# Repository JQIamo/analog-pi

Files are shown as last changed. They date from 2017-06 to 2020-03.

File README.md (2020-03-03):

# analog-pi
Analog PI controller with > 10MHz bandwidth. Design by Joe Tiamsuphat.

For full documentation of the circuit, see the [manual](https://github.com/JQIamo/analog-pi/blob/master/pi/Documents/PI_Manual.pdf).
Please read the manual very carefully, especially the section "Initial Calibration" at page 14. A wrong calibration could result in damaging the circuit's output stages.

**NOTE:** The PI controller [manual](https://github.com/JQIamo/analog-pi/blob/master/pi/Documents/PI_Manual.pdf) is out of date. It should still be used as a reference, but it does not document several new features. Please look at issues [#2](https://github.com/JQIamo/analog-pi/issues/2) and [#3](https://github.com/JQIamo/analog-pi/issues/3) for more information. 

## File description

* `/fab/*`: Ready-made files for immediate fabrication. There is the main PI board (`pi_v2.5.3`), and three "shield" boards which make assembly into the box (located in `/fab/EnclosureDesign_v2.5.3_CAD`) easier. See below for description.
* `/pi/*`: Design files for the main PI board, including documentation, schematics, simulations, etc. The schematic/board layout are done in NI Multisim + Ultiboard.
* `/pi-frontpanel/*`: Eagle board files for a frontpanel "shield" board
* `/pi-pots/*`: Eagle board files for potentiometers which set the gains, output offset, sweep amplitude.
* `/pi-shield/*`: Eagle board file for adapter shield between PI board and the POTs/Frontpanel breakout boards.

Total cost is in the neighborhood of $1k per completed box (includes professionally populated PCBs, enclosure, power supply, etc.), although that number would depend on quantity ordered, whether you populate the boards yourself, etc.

## Enclosure

There is a Protocase Designer file (in `/fab/EnclosureDesign_v2.5.3_CAD`

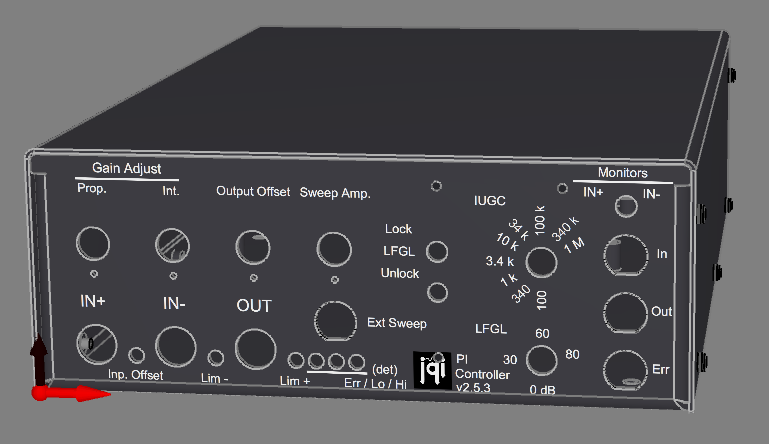
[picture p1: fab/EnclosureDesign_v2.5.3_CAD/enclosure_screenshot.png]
enclosure


Other auxiliary parts:

| Name | Part number | supplier |
|-------|------------|-------|
| FuseDrawer | 486-1342-ND | Digikey|
|Fuse	|F2393-ND|	Digikey|
|PwrEntry	|486-1302-ND	|Digikey
HexStandoff	|36-4802-ND|	Digikey
KnurledKnob	|226-3084-ND	|Digikey
POT Dial|	987-1002-ND	|Digikey
Isolated BNC	|ARFX1905-ND	|Digikey
PowerSupply	|179-2302-ND|	Digikey

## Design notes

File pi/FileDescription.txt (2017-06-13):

\Design\
   EnclosureDesign\			       -Enclosure design for version 2.4.1, 2.5.1, .2.5.2
      PanelCutout\                 -Sketchup: Enclosure cut-out designs
	  PI_EnclosureParts.xlsx       -Excel: Bill of Material for enclosure
   Gerber\                         -Gerber RS-274X, NC drill, Part-centroid export from PI.ewprj
   PartsDatabase\                  -MultiSim: Database containing parts schematics, footprints,
                                    and simulation models
   PartsMap\                       -Layout location map of resistors, capacitors, and IC.
   PI.ewnet                        -Ultiboard: netlist from Multisim to Ultiboard
   PI.ewprj                        -Ultiboard: Layout file
   PI.ms12                         -MultiSim: Schematic file
   PI_BOM_1MRInputImpedance.xlsx   -MS Excel: Bill of Material for PCB (1MOhm input impedance)
   PI_BOM_50RInputImpedance.xlsx   -MS Excel: Bill of Material for PCB (50Ohm input impedance)
   PI_Layout.pdf                   -PDF: Printout PCB layout images
   PI_Schematic.pdf                -PDF: Printout schematic design
\Document\
   PartsManual\                    -PDF: Data sheets of parts used in the project.
   TestResults2.5.1Mod\            -Test results of Modified2.5.1 (similar to 2.5.2)
   TestResults2.5Mod\              -Test results of Modified2.5 (similar to 2.5.1)
   PI_BodePlot.pxt                 -IGOR Pro: Interactive Bode plot of
                                    PI controller output response at different settings
   PI_Manual.docx                  -MS Word: Manual
   PI_Manual.pdf                   -PDF: Printout Manual
\Simulation\                       -MultiSim: Test simulations for models and designs
\FileDescription.txt               -Text: file description in the project
\VersionLog.txt                    -Text: Current version and change log

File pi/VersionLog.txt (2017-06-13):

Version 2.5.3

+ Add J9 low profile jumper to disable input offset.
+ Change part number for input offset POT (POT11) to one with low thermal coefficient. Adds ~$15 to BOM cost.

Version 2.5.2

+ Change IUGC capacitance. Remove 15uF and 4.7uF, add 470pF and 150pF
+ Add relay to turn off I_VGA when unlock.
+ Adjust Integral Limiter: change feedback capacitance from 510pF to 1500pF,
  and remove output capacitors
+ Change output impedance of monitor ports (IN_MON, ERR_MON, OUT_MON) from 1kOhm to 20 Ohms
  With 1 kOhm output impedance, monitor signals bandwidth are slower than the actual signal.
  To avoid confusion, using 20 Ohms output impedance makes the monitor ports show actual signals.
  However, output resistors can be damaged if monitor port is shorted-circuit. 

Version 2.5.1

+ Install 2 parallel 100 Ohms at OUT to make 50 Ohms output impedance,
  mitigating impedance mismatch and signal reflections.
+ Change input resistors to 2 parallel 100 Ohms to make it possible to modify input impedance.
  User can choose to install +/-10V 1 MOhm input impedance or +/-10V 50 Ohms input impedance.
+ Change maximum P_GAIN from 3 to 10

Fix issues in version 2.5

+ Correct wiring at regulators L7912 and L7905
+ I_VGA and P_VGA trims cannot zero the output offset.
  Change resistance around trim pot from 10kOhms to 3kOhms.
+ Unable to turn off P_GAIN and I_GAIN completely.
  Control voltage need to be at least -1.0V to turn off.
  Change resistance around external pot from 20kOhms to 10kOhms
  Increase control range to +/-1.7V to make sure that VGA can be completely turned off
+ High frequency signal ~10MHz pass through the integrator and destructive interfere
  with proportional signal
  Change input resistance to Integrator from 1kOhm to 10kOhms to reduce direct transfer signal.
+ Switch MON_IN1 causes oscillation in ERR_MON
  Long trace ERR_MON to LockDector makes LM7171 unstable.
  Install 1kOhm resistor to isolate output from long trace.
+ POT4 Buffer Bandwidth control is too close to output BNC and does not provide gain
  bandwidth limit as expected.  When use in low bandwidth mode, phase margin becomes worse.
  Use high bandwidth mode and install a 3MHz low-pass filter before buffer U18
+ LM7171 in OUTPUT stage has resonant response at 25MHz.
  Long trace PI to LockDector and IntLimiter makes LM7171 unstable
  Install 1kOhm resistor to isolate output from long trace.
+ Switch bouncing (IUGC, LFGL, UNLOCK/LFGL/LOCK).
  Install low-pass filter to mitigate switch bouncing.  Install MOSFETs for driving relays.
+ IN_MON, ERR_MON, OUT_MON overshoot at high frequency when connect 1m cable to oscilloscope.
  Install 1kOhm isolation resistors at output.  Expect monitor ports to drive high impedance load.

Version 2.5
   A prototype that aim to fix low-gain DC-offset issue in version 2.4.1.
The design implements separation between Proportional and Integral signals.
The separation between proportional and integral gives advantages over combined implementation:
+ Proportional signal can be faster and less noisy with less op-amp stages (10MHz->25MHz).
+ Integral signal can have higher open loop gain (80dB->120dB), minimizing DC offset
  from reference signal even with low proportional gain setting.
+ Allowing more flexible setting for slow(integral) and fast(proportional) signals.

This version also implements experimental design for feedback integral limiter, and output limiter.

Fine input offset is removed to use potentiometer knob for integral gain.

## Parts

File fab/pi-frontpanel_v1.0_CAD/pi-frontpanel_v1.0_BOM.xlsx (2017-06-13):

Line | Qty | Value | Part Num | Source | Package | Parts | Notes
1 | 1 |  | 450-1536-ND | Digikey | SP3T_LUG | S8_LOCK_UNLOCK
2 | 1 |  | A1921-ND | Digikey | 1X02 | JP2
3 | 1 |  | MMBT2222A-FDICT-ND | Digikey | SOT23-BEC | T1
4 | 1 |  | S7086-ND | Digikey | 2X18 | JP1
5 | 2 | 4.99k | P4.99KFCT-ND | Digikey | R_1206 | R2, R3
6 | 1 | 14k | P14.0KFCT-ND | Digikey | R_1206 | R1
7 | 4 | BNC-V | A32262-ND | Digikey | BNC-V | ERR_MON, IN_MON, OUT_MON, SWEEP_IN
8 | 2 | MRA112 | 360-2368-ND | Digikey | MRA112 | IUGC, LFGL
9 | 1 | SPDT | 450-1523-ND | Digikey | SPDT_LUG | S7_MON_IN_SEL
10 | 1 | SSL-LX5093IGW | 67-2207-ND | Digikey | LED-TH | LED | This part needs to be soldered such that the bottom of the LED is 0.6" (1.5cm) above the PCB surface.

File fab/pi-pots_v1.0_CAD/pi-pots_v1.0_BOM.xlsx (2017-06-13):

Line | Qty | Value | Part Num | Source | Package | Parts | Notes
1 | 4 | BOURNS-3590P | 3590P-1-103L-ND | Digikey | SP3T_LUG | I_GAIN, OUTPUT_OFFSET, P_GAIN, SWEEP_AMP
2 | 2 | PINHD-3X4 | 952-2121-ND | Digikey | 3x02 | J1 | This is a subassembly. Two 3x2 male headers are placed on bottom as marked on PCB.

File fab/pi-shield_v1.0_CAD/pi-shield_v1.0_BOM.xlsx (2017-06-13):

Line | Qty | Value | Part Num | Source | Package | Parts | Notes
1 | 1 |  | S2111EC-18-ND | Digikey | 2X18/90 | JP1
2 | 5 |  | S7000-ND | Digikey | 1X02 | J1_SWP_EXT, J4_IN_MON, J5_ERR_MON, J6_OUT_MON, LED1
3 | 2 |  | S7008-ND | Digikey | 1X10 | S5_IUGC, S6_LFGL
4 | 7 |  | S7036-ND | Digikey | 1X03 | J8_POW, POT7_SWP_AMP, POT8_OUT_OFFSET, POT9_IGAIN, POT10_PGAIN, S7_INPUT_MON_SW, S8_LOCK_UNLOCK
5 | 1 |  | A19470-ND | Digikey | 1X03 | J8_POW1
6 | 2 |  | S7071-ND | Digikey | 3X04 | J1 | This is a subassembly. Two 3x2 female headers are placed as marked on PCB.

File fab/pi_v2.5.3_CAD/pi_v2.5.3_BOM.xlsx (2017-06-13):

Quantity | Description | RefDes | Manufacturer | Manufacturer Part No. | Vendor | Vendor Part No. | Package | Type | Price | Total Price
3 | BNC | J2, J3, J7 | TE Connectivity | 1-1337543-0 | Digikey | A97553-ND | Ultiboard\1-1337543-0 | TH | 2.03000 | 6.09000
2 | HDR, HDR1X10 | S5, S6 | TE Connectivity | 1-640454-0 | Digikey | A19437-ND | Ultiboard\HDR_1-640454-0 | TH | 0.50000 | 1.00000
5 | HDR, HDR1X2 | J1, J4, J5, J6, LED1 | TE Connectivity | 640454-2 | Digikey | A19423-ND | Ultiboard\HDR_640454-2 | TH | 0.13000 | 0.65000
7 | HDR, HDR1X3 | J8, POT7, POT8, POT9, POT10, S7, S8 | TE Connectivity | 640454-3 | Digikey | A19430-ND | Ultiboard\HDR_640454-3 | TH | 0.17000 | 1.19000
1 | HDR, HDR1x3, 2mm low profile | J9 | Sullins Connector Solutions | NRPN031PAEN-RC | Digikey | S5800-03-ND | Ultiboard\HDR_2mm_3 | TH | 0.35000 | 0.35000
1 | POTENTIOMETER, ACCUTRIM 1280 | POT11 | Vishay Foil Resistors | Y005610K0000K0L | Digikey | 804-1021-ND | Ultiboard\3006P | TH | 17.84000 | 17.84000
5 | POTENTIOMETER, 3006P | POT4, POT5, POT6, POT12, POT13 | Bourns Inc. | 3006P-1-103LF | Digikey | 3006P-103LF-ND | Ultiboard\3006P | TH | 2.08000 | 10.40000
3 | POTENTIOMETER, 3296W | POT1, POT2, POT3 | Bourns Inc. | 3296W-1-102LF | Digikey | 3296W-102LF-ND | Ultiboard\3296W | TH | 2.41000 | 7.23000
4 | SWITCH, G5V-1-DC12 | S1, S2, S3, S4 | Omron Electronics Inc-EMC Div | G5V-1-DC12 | Digikey | Z774-ND | Ultiboard\G5V-1Relay | TH | 2.05000 | 8.20000
19 | CAPACITOR, 0.015uF | C35, C36, C37, C38, C39, C40, C41, C42, C43, C44, C45, C46, C47, C48, C49, C50, C51, C52, C115 | Murata Electronics North America | GRM155R71E153KA61D | Digikey | 490-3251-1-ND | Ultiboard\0402 | SMD | 0.03200 | 0.60800
1 | CAPACITOR, 0.047uF | C114 | Taiyo Yuden | TMK105B7473KV-F | Digikey | 587-2240-1-ND | Ultiboard\0402 | SMD | 0.01900 | 0.01900
92 | CAPACITOR, 0.15uF | C1, C2, C3, C4, C5, C6, C7, C11, C12, C13, C14, C15, C16, C17, C18, C19, C20, C23, C24, C25, C26, C31, C32, C33, C34, C53, C54, C55, C56, C57, C58, C59, C60, C61, C62, C63, C64, C65, C66, C67, C68, C69, C70, C71, C72, C73, C74, C75, C76, C77, C78, C79, C80, C81, C82, C83, C84, C85, C86, C87, C88, C89, C90, C91, C92, C93, C94, C95, C96, C97, C98, C109, C110, C113, C120, C121, C122, C123, C124, C125, C126, C127, C128, C129, C130, C131, C132, C133, C134, C135, C136, C137 | Samsung Electro-Mechanics America, Inc | CL10B154KA8SFNC | Digikey | 1276-1970-1-ND | Ultiboard\0603 | SMD | 0.01200 | 1.10400
1 | CAPACITOR, 0.47uF | C112 | Taiyo Yuden | TMK107B7474KA-TR | Digikey | 587-2670-1-ND | Ultiboard\0603 | SMD | 0.07200 | 0.07200
1 | CAPACITOR, 1.5uF | C111 | TDK Corporation | C1608X5R1E155K080AB | Digikey | 445-5962-1-ND | Ultiboard\0603 | SMD | 0.24000 | 0.24000
4 | CAPACITOR, 1500pF | C8, C9, C10, C117 | Murata Electronics North America | GRM155R71H152KA01J | Digikey | 490-6354-1-ND | Ultiboard\0402 | SMD | 0.02300 | 0.09200
9 | CAPACITOR, 150pF | C101, C102, C103, C104, C105, C106, C107, C108, C119 | Murata Electronics North America | GRM1555C1H151JA01D | Digikey | 490-3229-1-ND | Ultiboard\0403 | SMD | 0.03000 | 0.27000
8 | CAPACITOR, 15uF | C21, C22, C27, C28, C29, C30, C99, C100 | TDK Corporation | C2012X5R1V156M125AC | Digikey | 445-14423-1-ND | Ultiboard\0805 | SMD | 0.68900 | 5.51200
1 | CAPACITOR, 4700pF | C116 | Murata Electronics North America | GRM155R71E472KA01D | Digikey | 490-1309-1-ND | Ultiboard\0402 | SMD | 0.02100 | 0.02100
1 | CAPACITOR, 470pF | C118 | Murata Electronics North America | GRM1555C1H471JA01D | Digikey | 490-1297-1-ND | Ultiboard\0402 | SMD | 0.10000 | 0.10000
3 | MOSFET, 2N7002E | T1, T2, T3 | ON Semiconductor | 2N7002ET1G | Digikey | 2N7002ET1GOSCT-ND | Ultiboard\SOT-23-3 | SMD | 0.14000 | 0.42000
1 | OPAMP, BUF634 | U18 | Texas Instruments | BUF634U/2K5 | Digikey | 296-24142-1-ND | Ultiboard\SOIC8 | SMD | 8.13000 | 8.13000
1 | OPAMP, LM239 | U20 | Texas Instruments | LM239DR | Digikey | 296-14590-1-ND | Ultiboard\SOIC14 | SMD | 0.43000 | 0.43000
9 | OPAMP, LM7171 | U2, U5, U7, U10, U13, U16, U17, U28, U29 | Texas Instruments | LM7171AIMX/NOPB | Digikey | 296-35428-1-ND | Ultiboard\SOIC8 | SMD | 3.11100 | 27.99900
14 | OPAMP, OPA172 | U8, U12, U14, U15, U19, U21, U22, U23, U24, U25, U26, U27, U31, U32 | Texas Instruments | OPA172IDR | Digikey | 296-37237-1-ND | Ultiboard\SOIC8 | SMD | 1.68500 | 23.59000
4 | OPAMP, THS4631 | U1, U3, U4, U6 | Texas Instruments | THS4631D | Digikey | 296-17626-5-ND | Ultiboard\SOIC8 | SMD | 10.55000 | 42.20000
2 | OPAMP, VCA824 | U9, U11 | Texas Instruments | VCA824ID | Digikey | 296-22898-5-ND | Ultiboard\SOIC14 | SMD | 9.45000 | 18.90000
35 | RESISTOR, 100kΩ | R51, R52, R70, R71, R73, R74, R77, R78, R85, R86, R87, R88, R89, R90, R92, R93, R96, R97, R98, R99, R100, R101, R102, R103, R104, R109, R114, R115, R116, R117, R118, R119, R120, R121, R122 | Rohm Semiconductor | MCR03ERTF1003 | Digikey | RHM100KCFCT-ND | Ultiboard\0603 | SMD | 0.00840 | 0.29400
3 | RESISTOR, 100Ω | R64, R65, R66 | Vishay Thin Film | PHP01206E1000BST5 | Digikey | PHP100ACT-ND | Ultiboard\VTFR1206 | SMD | 3.53000 | 10.59000
13 | RESISTOR, 10kΩ | R25, R36, R42, R53, R54, R55, R56, R81, R82, R83, R84, R91, R107 | Rohm Semiconductor | MCR03ERTF1002 | Digikey | RHM10.0KCFCT-ND | Ultiboard\0603 | SMD | 0.01100 | 0.14300
1 | RESISTOR, 10MΩ | R113 | Rohm Semiconductor | MCR03ERTJ106 | Digikey | RHM10MCGCT-ND | Ultiboard\0603 | SMD | 0.01000 | 0.01000
22 | RESISTOR, 1kΩ | R15, R16, R17, R18, R26, R29, R40, R45, R46, R48, R49, R50, R57, R58, R59, R60, R69, R75, R76, R79, R80, R105 | Vishay Beyschlag | MCT06030C1001FP500 | Digikey | MCT0603-1.00K-CFCT-ND | Ultiboard\0603 | SMD | 0.06900 | 1.51800
3 | RESISTOR, 1MΩ | R3, R10, R111 | Samsung Electro-Mechanics America, Inc | RC1608F105CS | Digikey | 1276-3487-1-ND | Ultiboard\0603 | SMD | 0.01400 | 0.04200
10 | RESISTOR, 20Ω | R5, R12, R19, R24, R30, R35, R43, R44, R47, R61 | Rohm Semiconductor | MCR03ERTF20R0 | Digikey | RHM20CFCT-ND | Ultiboard\0603 | SMD | 0.01100 | 0.11000
1 | RESISTOR, 300kΩ | R110 | Rohm Semiconductor | MCR03ERTF3003 | Digikey | RHM300KCFCT-ND | Ultiboard\0603 | SMD | 0.01100 | 0.01100
2 | RESISTOR, 30kΩ | R72, R108 | Rohm Semiconductor | MCR03ERTF3002 | Digikey | RHM30KCFCT-ND | Ultiboard\0603 | SMD | 0.01100 | 0.02200
9 | RESISTOR, 3kΩ | R20, R21, R22, R23, R27, R33, R34, R37, R106 | Rohm Semiconductor | MCR03ERTF3001 | Digikey | RHM3.00KCFCT-ND | Ultiboard\0603 | SMD | 0.01100 | 0.09900
1 | RESISTOR, 3MΩ | R112 | Rohm Semiconductor | MCR03ERTJ305 | Digikey | RHM3MCGCT-ND | Ultiboard\0603 | SMD | 0.01000 | 0.01000
18 | RESISTOR, 402Ω | R1, R2, R6, R7, R8, R9, R13, R14, R31, R32, R38, R39, R62, R63, R67, R68, R94, R95 | Vishay Thin Film | PHP00603E4020BST1 | Digikey | 764-1092-1-ND | Ultiboard\VTFR0603 | SMD | 1.35440 | 24.37920
2 | RESISTOR, 604Ω | R28, R41 | Rohm Semiconductor | MCR03ERTF6040 | Digikey | RHM604CLCT-ND | Ultiboard\0603 | SMD | 0.01100 | 0.02200
5 | SWITCH, ADG1412 | S9, S10, S11, S12, S13 | Analog | ADG1412YRUZ | Digikey | ADG1412YRUZ-ND | Ultiboard\TSSOP16 | SMD | 7.17000 | 35.85000
13 | SWITCHING_DIODE, MMBD1203 | D1, D2, D3, D4, D5, D6, D7, D8, D9, D10, D11, D12, D13 | Fairchild Semiconductor | MMBD1203 | Digikey | MMBD1203CT-ND | Ultiboard\SOT-23-3 | SMD | 0.20500 | 2.66500
1 | VOLTAGE_REFERENCE, ADR445 | U30 | Analog Devices | ADR445ARZ | Digikey | ADR445ARZ-ND | Ultiboard\SOIC8 | SMD | 6.25000 | 6.25000
1 | VOLTAGE_REGULATOR, L7805 | U36 | STMicroelectronics | L7805ACD2T-TR | Digikey | 497-7253-1-ND | Ultiboard\D2PAK | SMD | 0.72000 | 0.72000
1 | VOLTAGE_REGULATOR, L7812 | U34 | STMicroelectronics | L7812ACD2T-TR | Digikey | 497-1177-1-ND | Ultiboard\D2PAK | SMD | 0.87000 | 0.87000
1 | VOLTAGE_REGULATOR, L7905 | U35 | STMicroelectronics | L7905CD2T-TR | Digikey | 497-1214-1-ND | Ultiboard\D2PAK | SMD | 0.87000 | 0.87000
1 | VOLTAGE_REGULATOR, L7912 | U33 | STMicroelectronics | L7912CD2T-TR | Digikey | 497-1215-1-ND | Ultiboard\D2PAK | SMD | 0.83000 | 0.83000
 |  |  |  |  |  |  |  |  |  | 267.96220
 | BOARD SUMMARY
 | Total number of unique parts | 45
 | SMD placements per board | 314
 | TH placements per board | 31

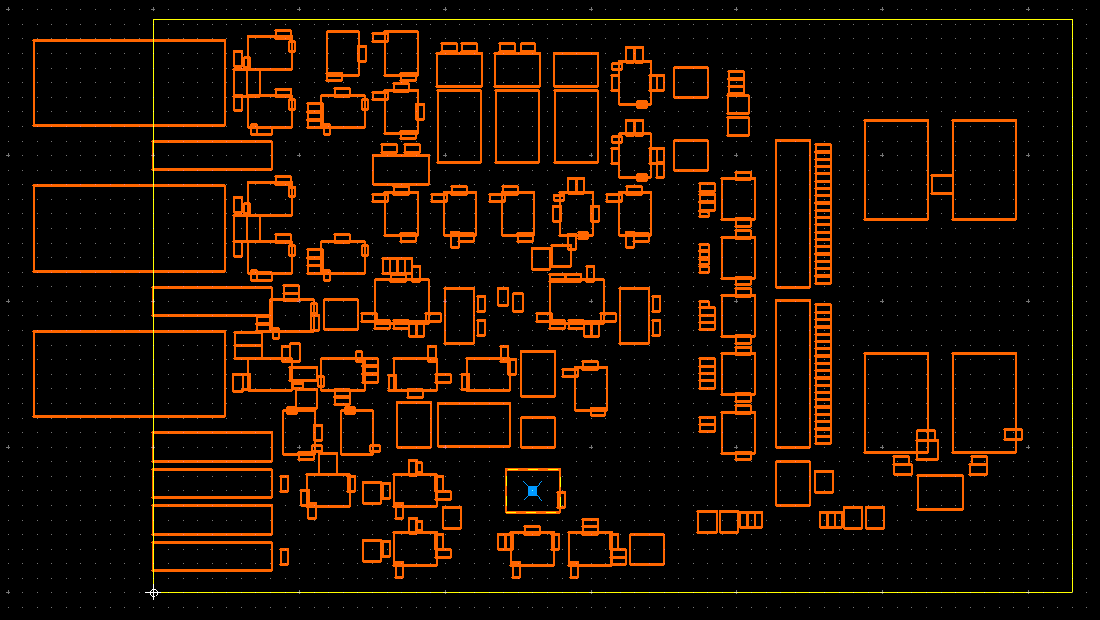
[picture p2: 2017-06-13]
pi/Design/PartsMap/ICMap/LM239.png

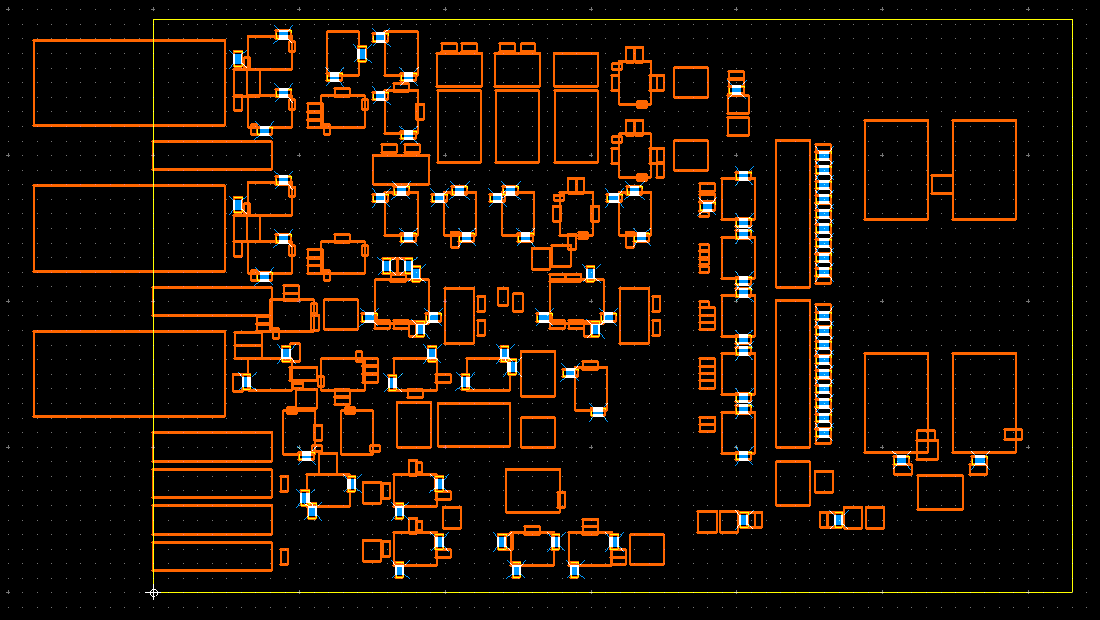
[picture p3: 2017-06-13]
pi/Design/PartsMap/CMap/0.15uF.png

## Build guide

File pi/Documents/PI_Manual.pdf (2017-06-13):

1

## PROPORTIONAL INTEGRAL CONTROLLER 2.5.2

## MANUAL

May 2016

Jiraphat Tiamsuphat
jt6ab@umd.edu

2

## Table of Contents

3

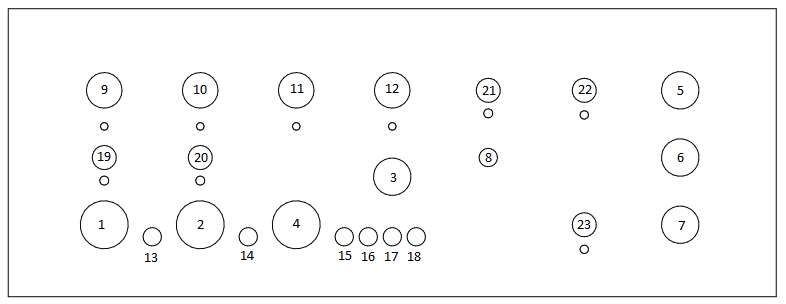
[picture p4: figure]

4

### Front Panel

Inputs

### 1. IN1 - Positive input (±10V, 1MΩ input impedance) 2. IN2 - Negative input (±10V, 1MΩ input impedance) 3. SWP_EXT - External sweep input (±10V, 10kΩ Input Impedance)

Outputs

### 4. OUT - PI filtered output signal (50Ω output impedance) 5. IN_MON - Monitor selected input voltage IN1/IN2 6. ERR_MON - Monitor error voltage 7. OUT_MON - Monitor output voltage

× ܯ_ =

Ω
Indicator

### 8. LED - lock indicator (Green/Red)

Controls
Potentiometer Knobs

### 9. I_GAIN - Integral gain control (Gain Range:0→10 with Dial: 20→80) 10. P_GAIN - Proportional gain control (Gain Range:0→10 with Dial: 20→80) 11. OUT_OFFSET - Output offset voltage control (±10.0V) 12. SWP_AMP - Sweep amplitude control

Front Panel Trimmer Potentiometers

### 13. IN_OFFSET - Input offset voltage control (±5.0V) 14. LO_LIMIT - Low limit of OUT (±10V) 15. HI_LIMIT - High limit of OUT (±10V) 16. ERR_DET - Absolute limit detection of error signal (Range: ±0→±1.5V) 17. LO_DET - Low limit detection of OUT 18. HI_DET - High limit detection of OUT

Switches

19. Unused switch (Fine input offset switch in version 2.4.1) 20. IN_MON_SEL (2 Positions) - Select to monitor IN1 (up) or IN2 (down) 21. LOCK/LFGL/UNLOCK (3 Positions) - Select filter mode 22. IUGC (9 Positions) - Select integral unity gain cutoff frequency 23. LFGL (9 Positions) - Select integral gain limit in LFGL mode

5

### Controls

Integral
I_GAIN
Continuous integral gain setting (I_GAIN: 0→10 with Dial: 20→80) In typical usage, I_GAIN should be set at 10 or as high as possible. IUGC (Integral Unity Gain Cutoff)
Select setting for integral unity gain cutoff
IUGC Unity Gain Cutoff frequency = (I_GAIN=3→10)
1* | 34 Hz → 100 Hz
2* | 100 Hz → 340 Hz
3* | 340 Hz → 1 kHz
4* | 1 kHz → 3.4 kHz
5 3.4 kHz → 10 kHz
6 10 kHz → 34 kHz
7 34 kHz → 100 kHz
8 100 kHz → 340 kHz
9† 340 kHz → 1 MHz
* Proportional gain must be turned off
† Proportional gain must be turned on
LFGL (Low Frequency Gain Limit)
Select setting for Low Frequency Gain Limit. Position LFGL = 20 Log(
| Ω ) (I_GAIN=3→10)
1 -10dB → 0dB
2 0dB → 10dB
3 10dB → 20dB
4 20dB → 30dB
5 30 dB → 40dB
6 40dB → 50dB
7 50 dB → 60dB
8 60 dB → 70dB
9 70 dB → 80dB

Determine Suitable Integral Settings
In negative feedback control scheme, high gain is required to make system signal close to equal the reference signal. Fast signal response is also desired to make system signal follow reference signal as fast as possible. However, if the gain of the feedback system is too high and too fast (gain higher than 0dB at 0 degree phase margin), the feedback system will become unstable and oscillate.

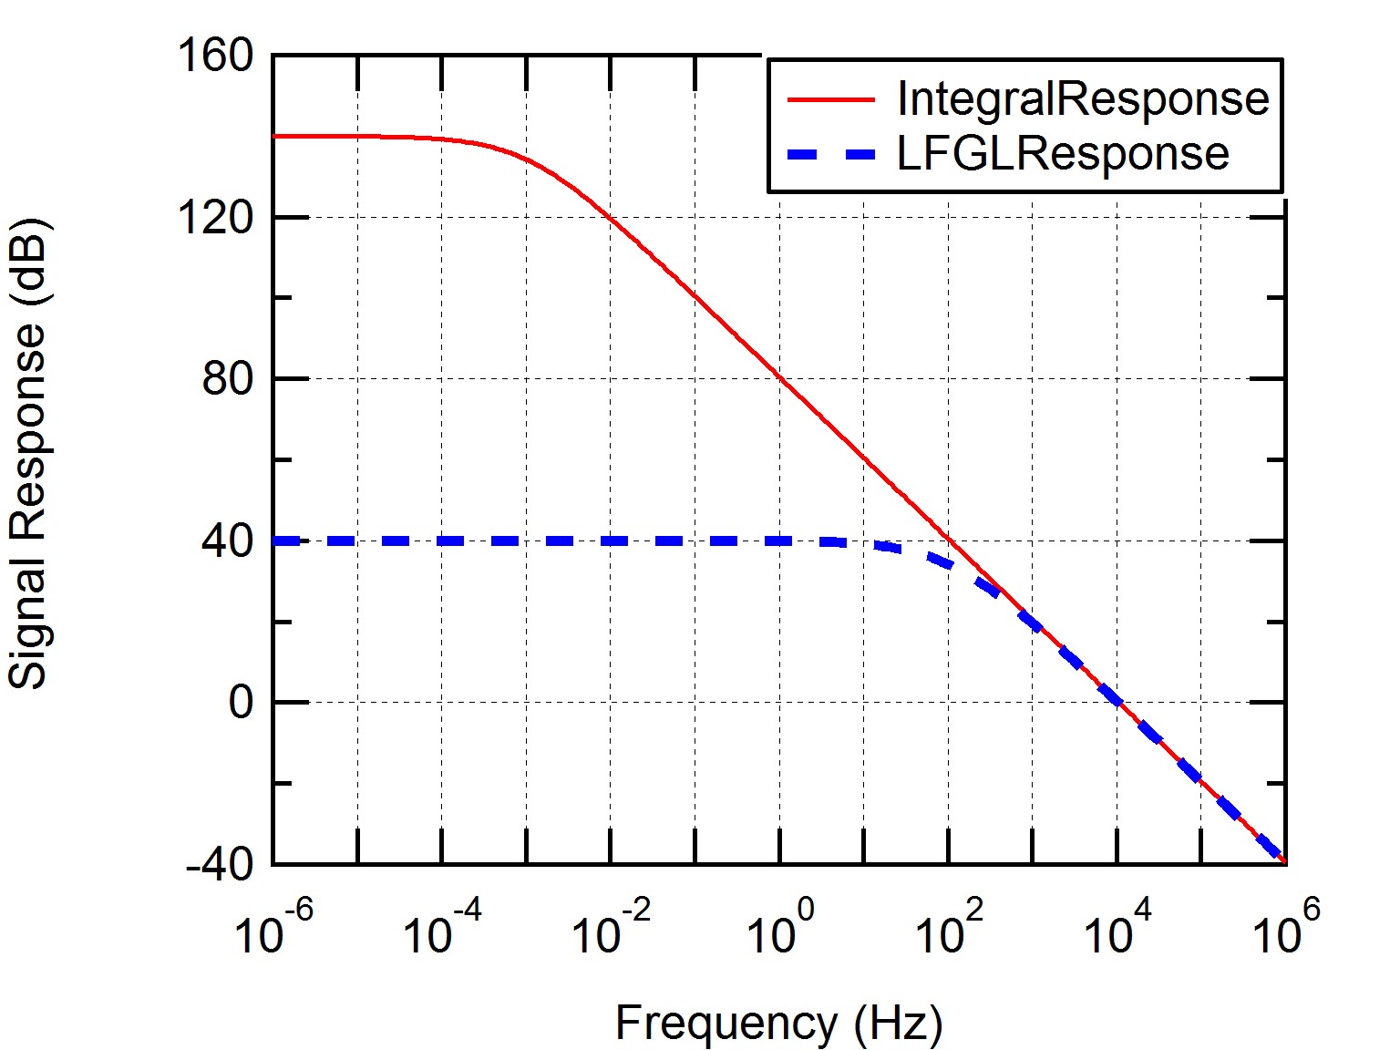
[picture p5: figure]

6

To find suitable Integral setting, first, try locking the system with the following setting I_GAIN=10, IUGC=8, LFGL=9, P_GAIN=0.
If the system oscillate with this setting, try the following
1. Set mode to LFGL and reduce LFGL setting.
2. Use lower IUGC setting and repeat 1.

### 3. Use lower I_GAIN setting (I_GAIN lower than 3 is not recommended)

If the system cannot be locked with the setting I_GAIN=1, IUGC=1, LFGL=1, P_GAIN=0, the system may be too slow to be locked with this controller.
Bode Plot of Integral Signal Response
The following are examples integral response at different settings. The interactive plotting code (Igor pro) can be found at \Documents\PI_BodePlot.pxt

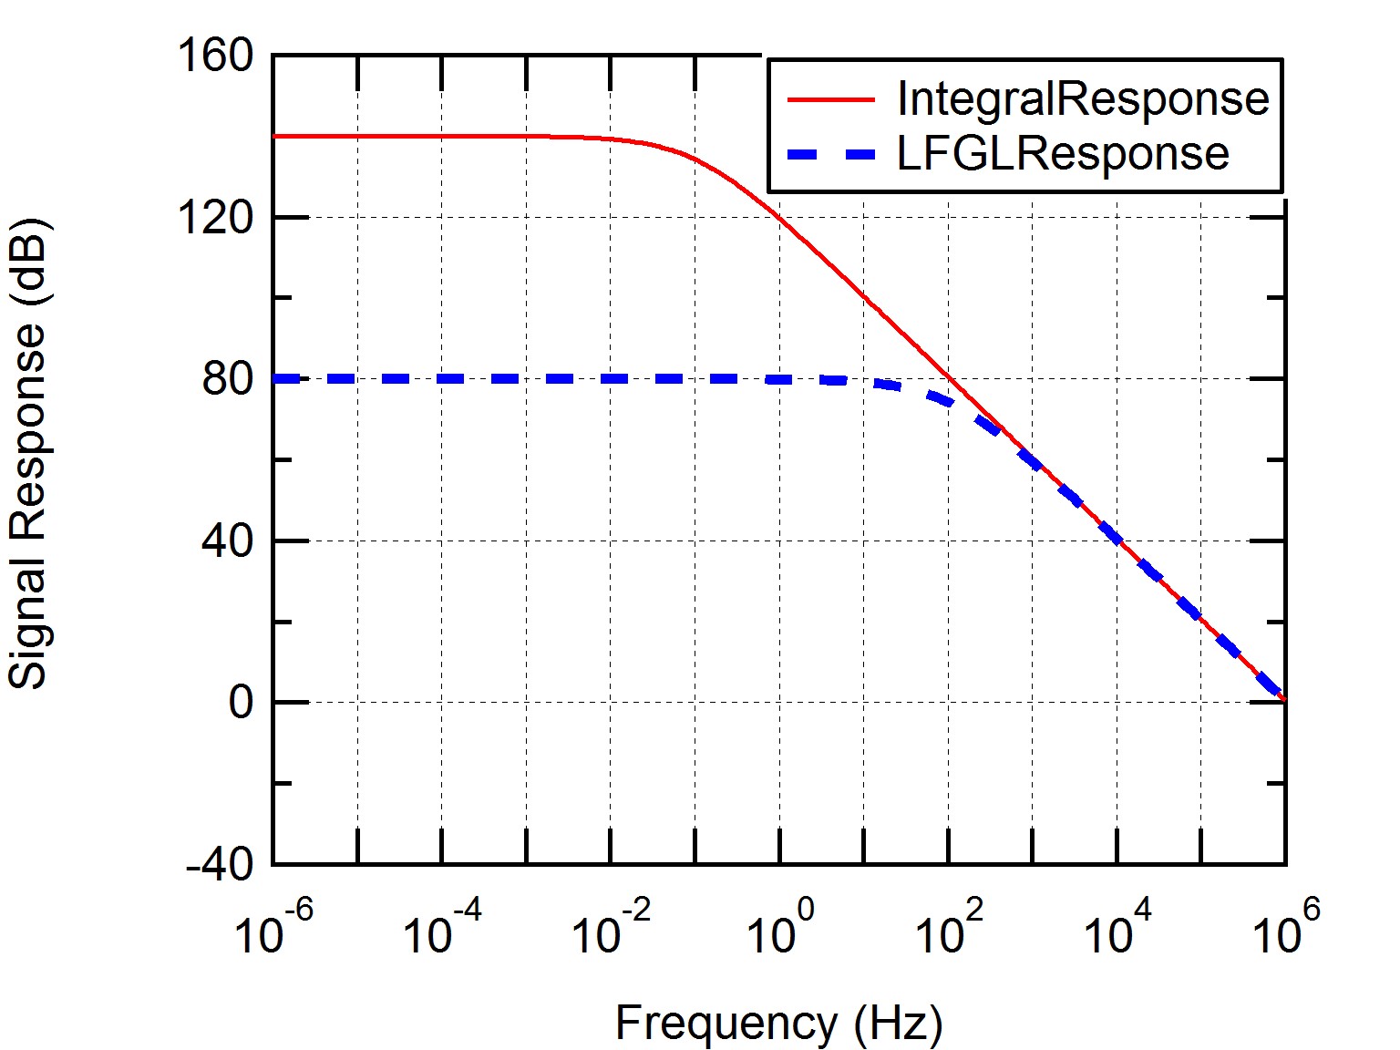
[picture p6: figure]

I_GAIN=10,
IUGC(9)=1MHz, LFGL(9)=80dB

I_GAIN=10,
IUGC(5)= 10kHz, LFGL(5)=40dB

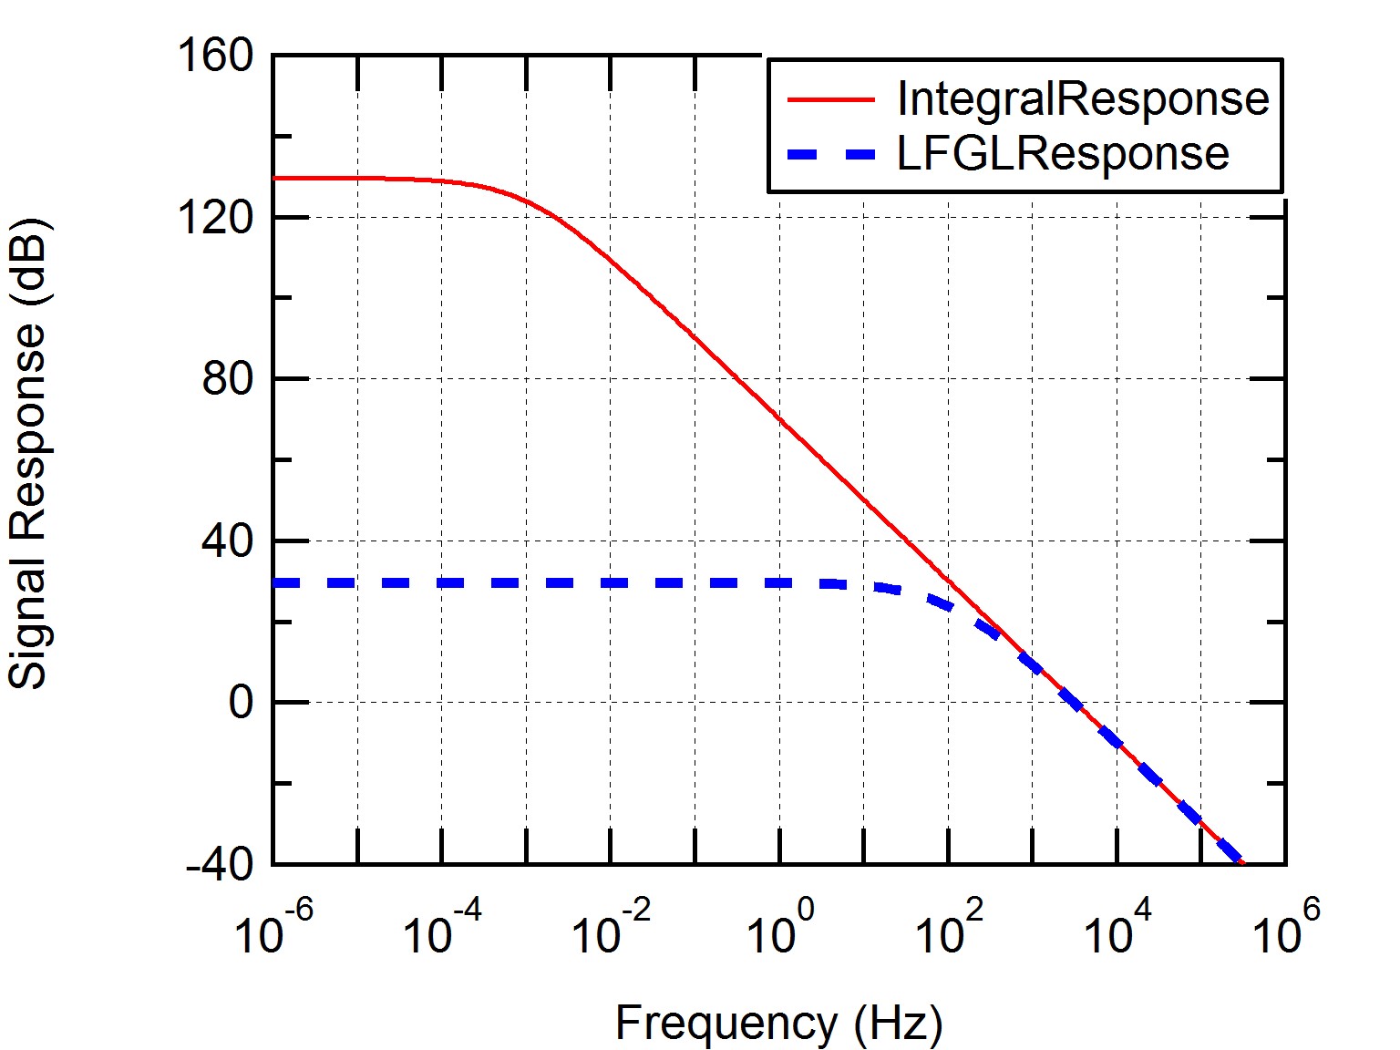
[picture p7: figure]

I_GAIN=3,
IUGC(5)= 3kHz, LFGL(5)=30dB

Proportional
P_GAIN
Continuous proportional gain setting (P_GAIN: 0→10 with Dial: 20→80)
While the integral signal has unity gain bandwidth up to 1 MHz, the proportional signal has unity gain bandwidth between 1 kHz to 10 MHz. Due to high speed nature of Proportional signal, if P_GAIN is too high (P_GAIN*SYSTEM_GAIN > 0dB), it may cause an oscillation on system that has response bandwidth less than 20MHz.
To find suitable P_GAIN setting, first, set P_GAIN=0 and lock the system using only the integral signal. Then, slowly increase P_GAIN until OUT start to oscillate. The suitable setting for P_GAIN is 90-95% of P_GAIN that makes OUT oscillate.

7

Operation Mode
UNLOCK: Switch Down
OUT is set by OUT_OFFSET, SWP_EXT, and SWP_AMP. Output scan is active
LFGL: Switch Middle
Output scan is active.
PI filter is active with limited low frequency gain
LOCK: Switch Up
Output scan is inactive.
PI filter is active with 120dB + I_GAIN[dB] low frequency gain. Operation Formula
ERR = IN1 − IN2 + IN_OFFSET
SWP = SWP_AMP × SWP_EXT
P = P_GAIN × (IN1 − IN2) | for signal frequency 100 Hz to 10MHz
UNLOCK: OUT = OUT_OFFSET + SWP
LFGL: | OUT = OUT_OFFSET + SWP + P + LFGL[I_GAIN × ERR]
LOCK: | OUT = OUT_OFFSET + P + INT[I_GAIN × ERR]
| LFGL is the integration with limited gain
| INT is the open-loop integration

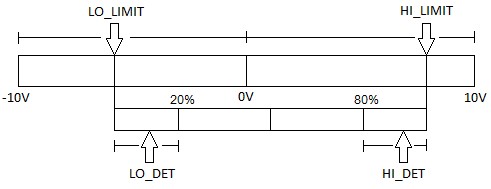
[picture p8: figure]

8

Miscellaneous Setting
LO_LIMIT/HI_LIMIT
The trim potentiometers set the low/high limit of OUT signal. To set the output range:

### 1. Disconnect IN1 and IN2, Monitor voltage value of OUT 2. Set filter mode to LOCK 3. Turn IN_OFFSET clockwise until OUT increases to high limit 4. Adjust HI_LIMIT to desire level 5. Turn IN_OFFSET counter-clockwise until OUT decreased to low limit 6. Adjust LO_LIMIT to desire level

ERR_DET
The LED indicator will become red if the value of ERR_MON is outside the range of ERR_DET (Variable Range: ±0→±4V).
LO_DET/HI_DET
The LED indicator will become red if the signal OUT is greater than HI_DET or lower than LO_DET. HI_DET can be set from 80% to 100% of output range. LO_DET can be set from 0% to 20% of output range.

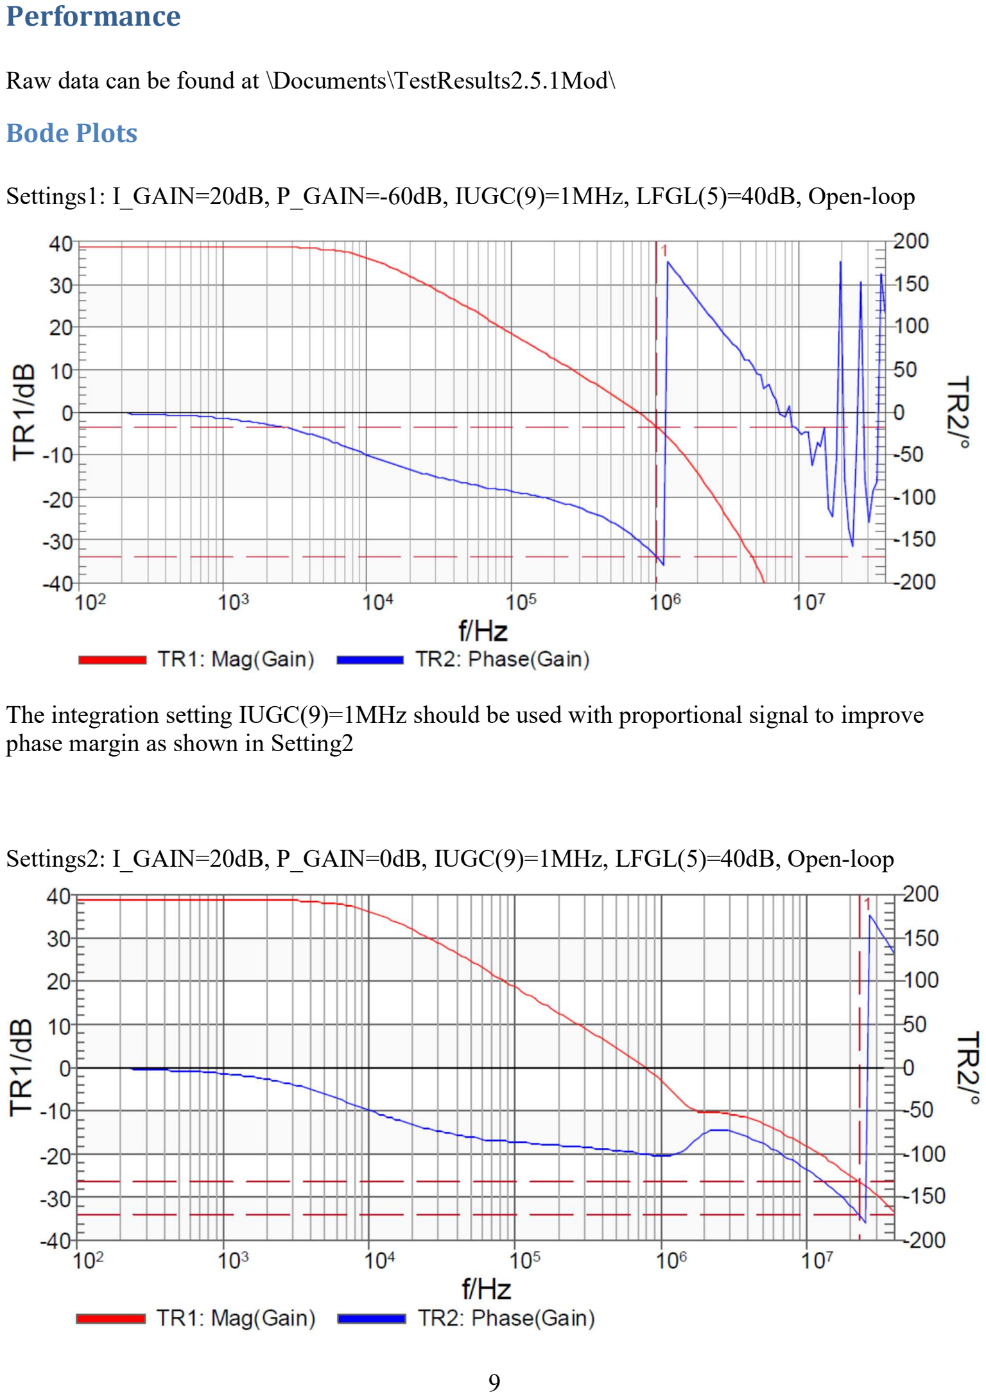
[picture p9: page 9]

9

### Performance

Raw data can be found at \Documents\TestResults2.5.1Mod\
Bode Plots
Settings1: I_GAIN=20dB, P_GAIN=-60dB, IUGC(9)=1MHz, LFGL(5)=40dB, Open-loop

The integration setting IUGC(9)=1MHz should be used with proportional signal to improve phase margin as shown in Setting2

Settings2: I_GAIN=20dB, P_GAIN=0dB, IUGC(9)=1MHz, LFGL(5)=40dB, Open-loop

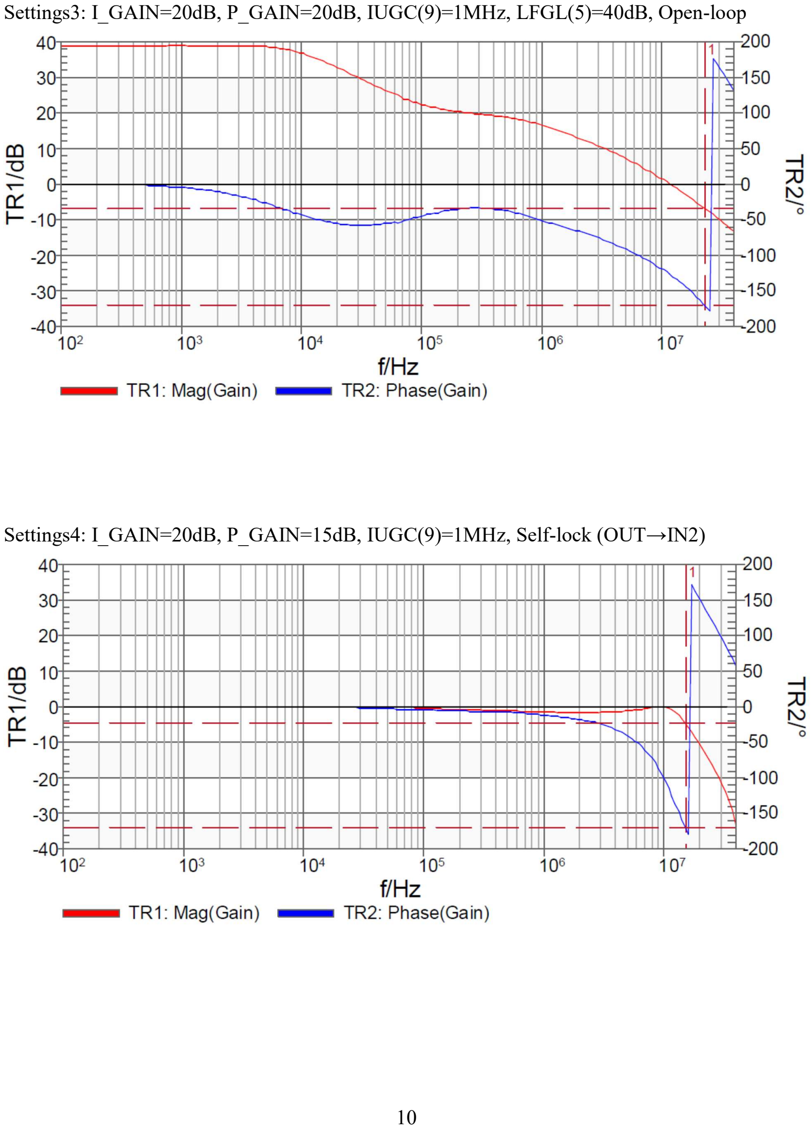
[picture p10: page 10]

10

Settings3: I_GAIN=20dB, P_GAIN=20dB, IUGC(9)=1MHz, LFGL(5)=40dB, Open-loop

Settings4: I_GAIN=20dB, P_GAIN=15dB, IUGC(9)=1MHz, Self-lock (OUT→IN2)

11

Self-Lock to Changing Reference
Use settings: I_GAIN=20dB, P_GAIN=10-20dB, IUGC(9)=1MHz, Self-lock (OUT→IN2) Blue: Reference signal (IN1)
Yellow: Reference Input monitor signal (IN1_MON)
Green: Output monitor signal (OUT_MON)

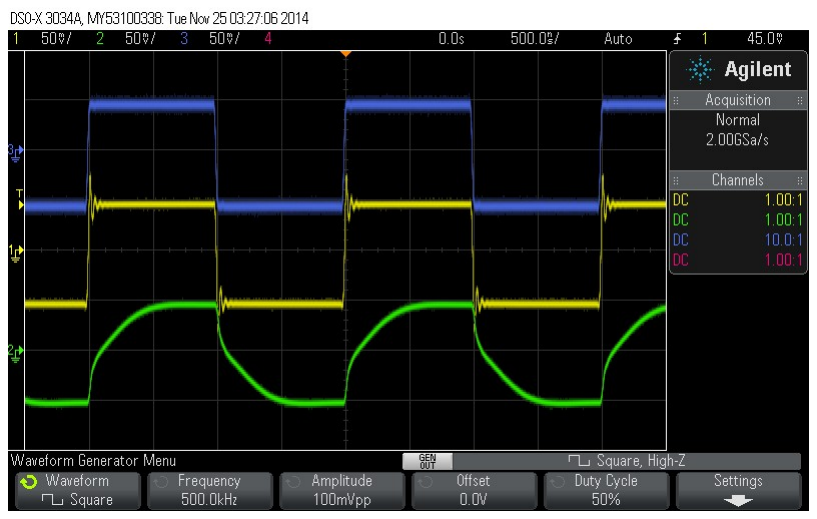
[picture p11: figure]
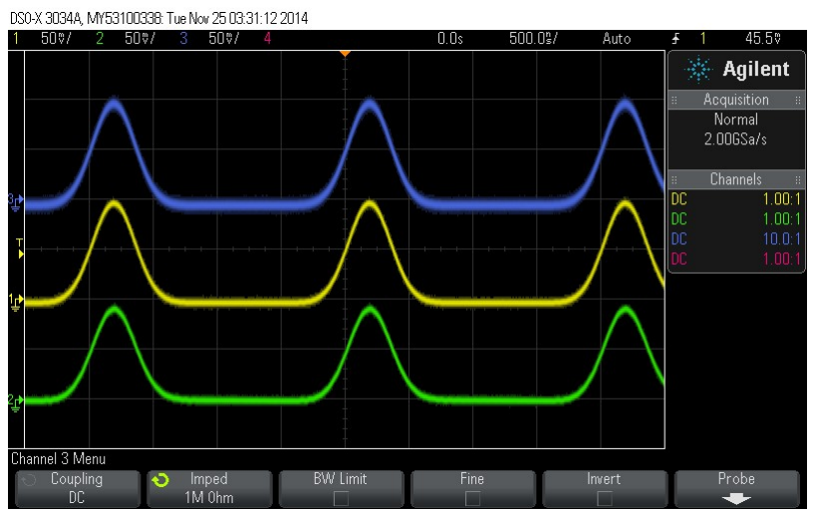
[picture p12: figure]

X-axis=500ns/div Y-axis=50mV/div | X-axis=500ns/div Y-axis=50mV/div

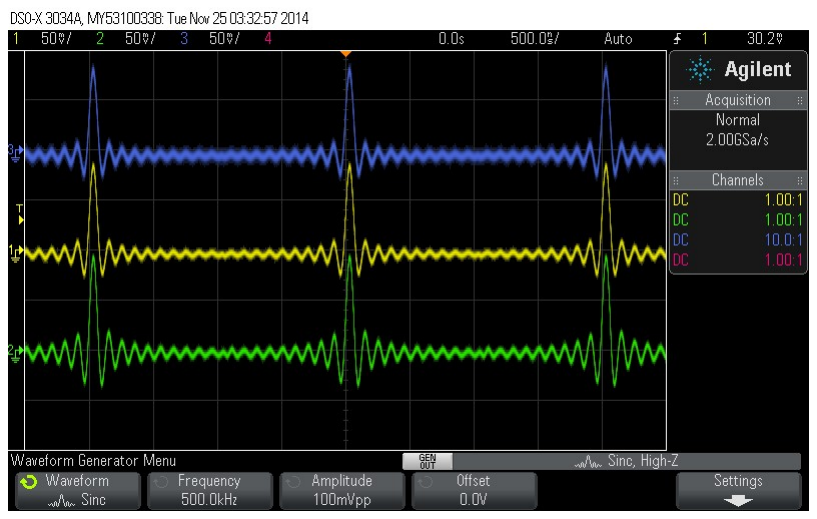
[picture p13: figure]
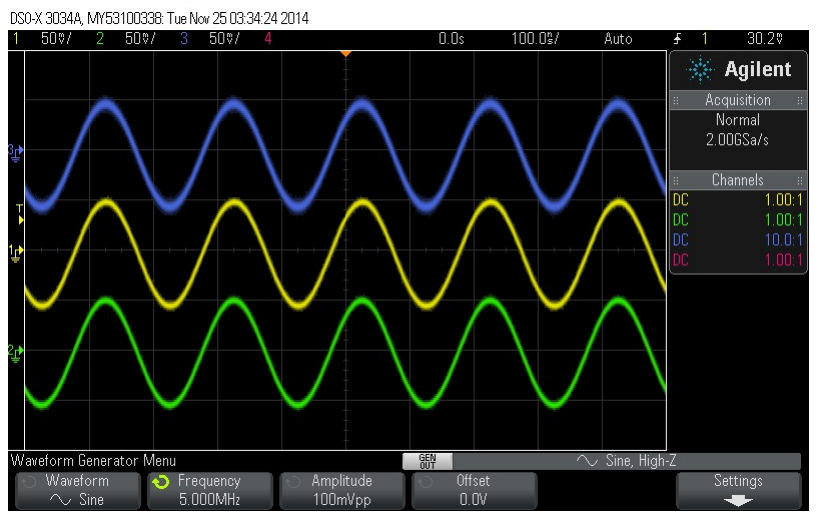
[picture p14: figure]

X-axis=500ns/div Y-axis: 50mV/div | X-axis=100ns/div Y-axis: 50mV/div
Test with large change in reference (±2.5V)
Yellow: Reference Input monitor signal (IN1_MON)
Green: Output monitor signal (OUT_MON)

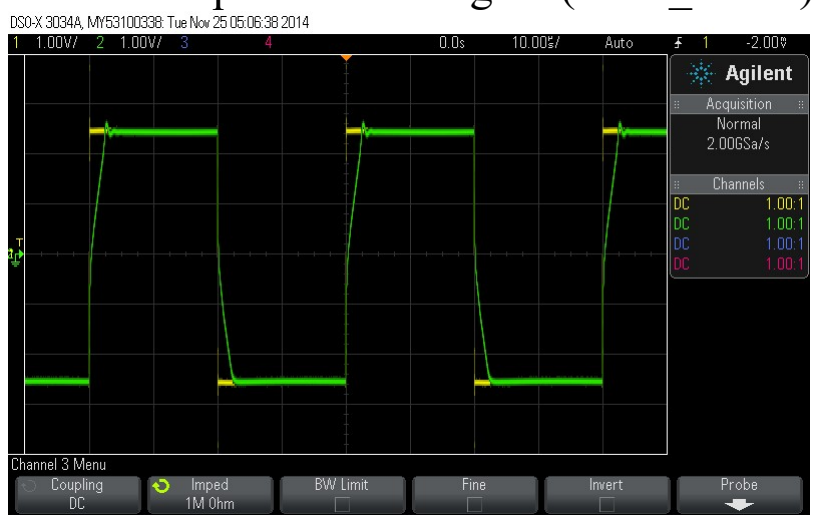
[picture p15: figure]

X-axis=10us/div Y-axis: 1V/div

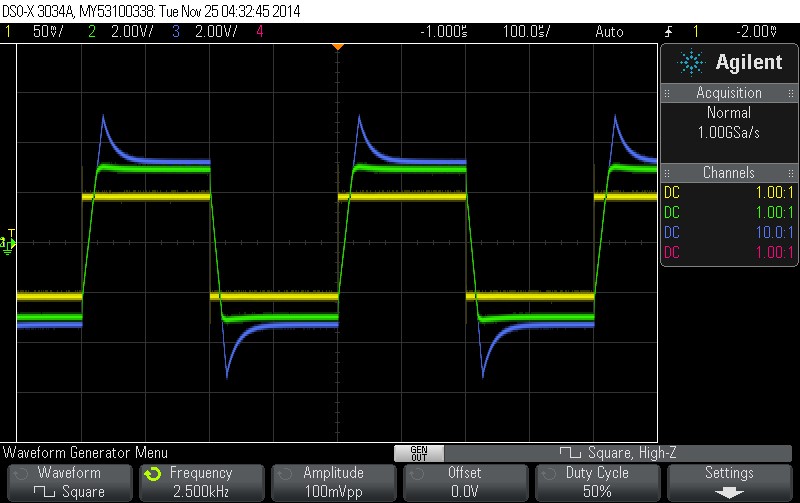
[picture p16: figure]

12

Integral Limiter and Output Limiter
Use settings: I_GAIN=20dB, P_GAIN=0dB, IUGC(9)=1MHz, LFGL(5)=40dB, Open-loop Set output high limit to +3V and output low limit to -3V
Yellow: Error monitor signal (ERR_MON)
Green: Output monitor signal (OUT_MON)
Blue: Output detection signal (OUT_DET)
OUT_DET is the output signal before output limiter; this signal is used for integral limiter.
When OUT_DET passes the output limits, it activates integral limiter that will stop the integrator from integrating signal further away from output limit. The output signal always stay inside the limit. However, OUT_DET may overshoot pass the output limit and recover back to stay slightly outside the output limit.

13

### Assembly

Front Panel Connection
RefDes | Front Panel Function
J1 | External Sweep
J4 | Input Monitor
J5 | Error Monitor
J6 | Output Monitor
LED1 | Red/Green LED
| 1 = GREEN P-doped (Anode)
| 2 = RED P-doped (Anode)
POT7 | Sweep Amplitude
POT8 | Output Offset
POT9 | Integral Gain
POT10 | Proportional Gain
S6 | Input Monitor Select
| 2→1 (D) = Monitor Input2
| 2→3 (U) = Monitor Input1
S4 | IUGC setting
| 1→2 = IUGC1
| 1→3 = IUGC2
| 1→4 = IUGC3
| 1→5 = IUGC4
| 1→6 = IUGC5
| 1→7 = IUGC6
| 1→8 = IUGC7
| 1→9 = IUGC8
| 1→10 = IUGC9
S5 | LFGL setting
| 1→2 = LFGL1
| 1→3 = LFGL2
| 1→4 = LFGL3
| 1→5 = LFGL4
| 1→6 = LFGL5
| 1→7 = LFGL6
| 1→8 = LFGL7
| 1→9 = LFGL8
| 1→10 = LFGL9
S7 | Unlock/LowFrequencyGainLimit/Lock
| SP3T Connections: Pin1→1, Pin2→2, Pin3→Pin5, Pin4→3
| 2→ (U) = Lock
| 2→3 (M) = LFGL
| 2→1 (D) = Unlock

14

Initial Calibrations and Tests
Power up:

### 1. Connect all front panel controls to the board 2. Connect OUT_MON to oscilloscope to monitor output voltage for initial testing 3. Turn on power supply to the board 4. The board should use around 300mA from +15V and 260mA from -15V. If you use test

power supply, set the current limit to 800mA to both +15V and -15V.
5. Change OUT_OFFSET to set OUT_MON to 0V.
Setup HI_LIMIT and LO_LIMIT:
6. Set mode to LOCK.
a. If OUT_MON decrease after set mode to LOCK, OUT_MON is at LO_LIMIT
b. If OUT_MON increase after set mode to LOCK, adjust IN_OFFSET CCW until OUT_MON decrease to LO_LIMIT

### 7. Change LO_LIMIT to set OUT_MON to -6V 8. Adjust IN_OFFSET CW until OUT_MON increase to HI_LIMIT 9. Change HI_LIMIT to set OUT_MON to +6V

Proportional VGA calibration: See picture next page

### 10. Set mode to UNLOCK 11. Use probe to measure the output pin (U9—Pin10) 12. Adjust the output of the VGA (U9—Pin10) to 0V with P_VGA_OUT_TRIM (POT2) 13. Set mode to LOCK, Set P_GAIN to maximum 14. Adjust the output of the VGA (U9—Pin10) to 0V with P_VGA_IN_TRIM (POT1)

Integral VGA calibration:

### 15. Measure OUT_MON voltage 16. Set mode to LFGL with this setting I_GAIN = 0, P_GAIN = 0, IUGC(7), LFGL(5) 17. Adjust OUT_MON to 0V with I_VGA_OUT_TRIM (POT3)

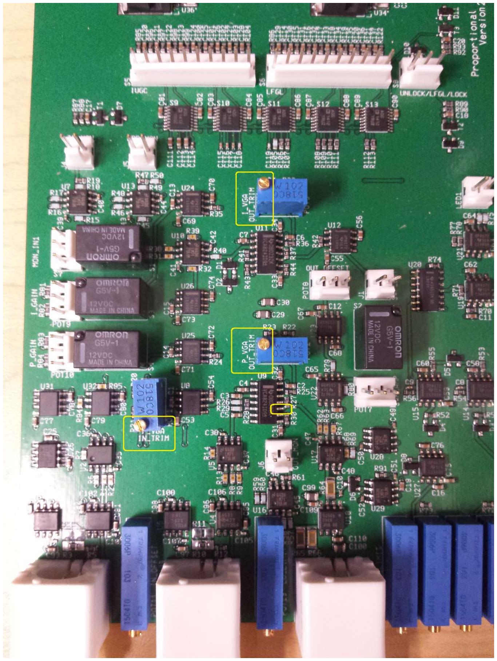
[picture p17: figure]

15

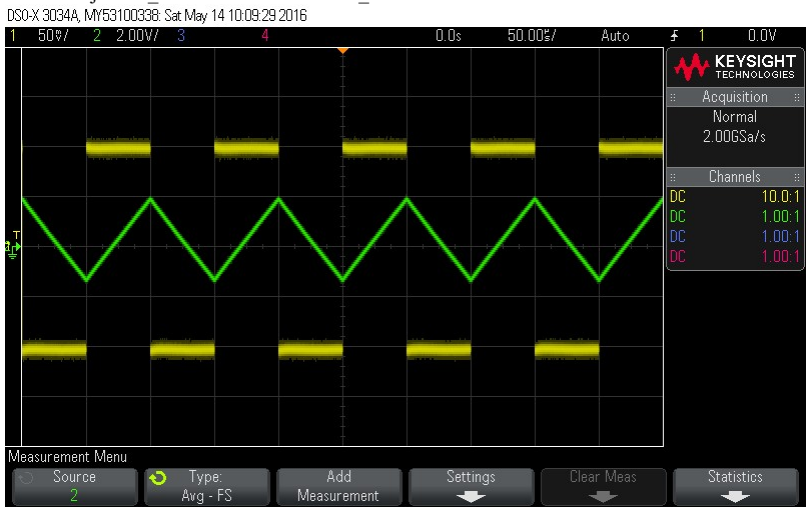
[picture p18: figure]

16

Square wave reference test:

18. Generate a 10kHz square wave 0.2Vpp (reference signal) 19. Send the reference signal to IN1 (Positive input) 20. Connect IN_MON to oscilloscope to monitor IN1 21. Set mode to LFGL with this setting I_GAIN = Max, P_GAIN = 0, IUGC(7), LFGL(7) 22. OUT_MON should show triangle wave (integral of square wave)

a. Yellow = reference signal
b. Green = OUT_MON
c. Output may be clipped at output limit

### 23. Adjust IN_OFFSET to set the OUT_MON to center at 0V

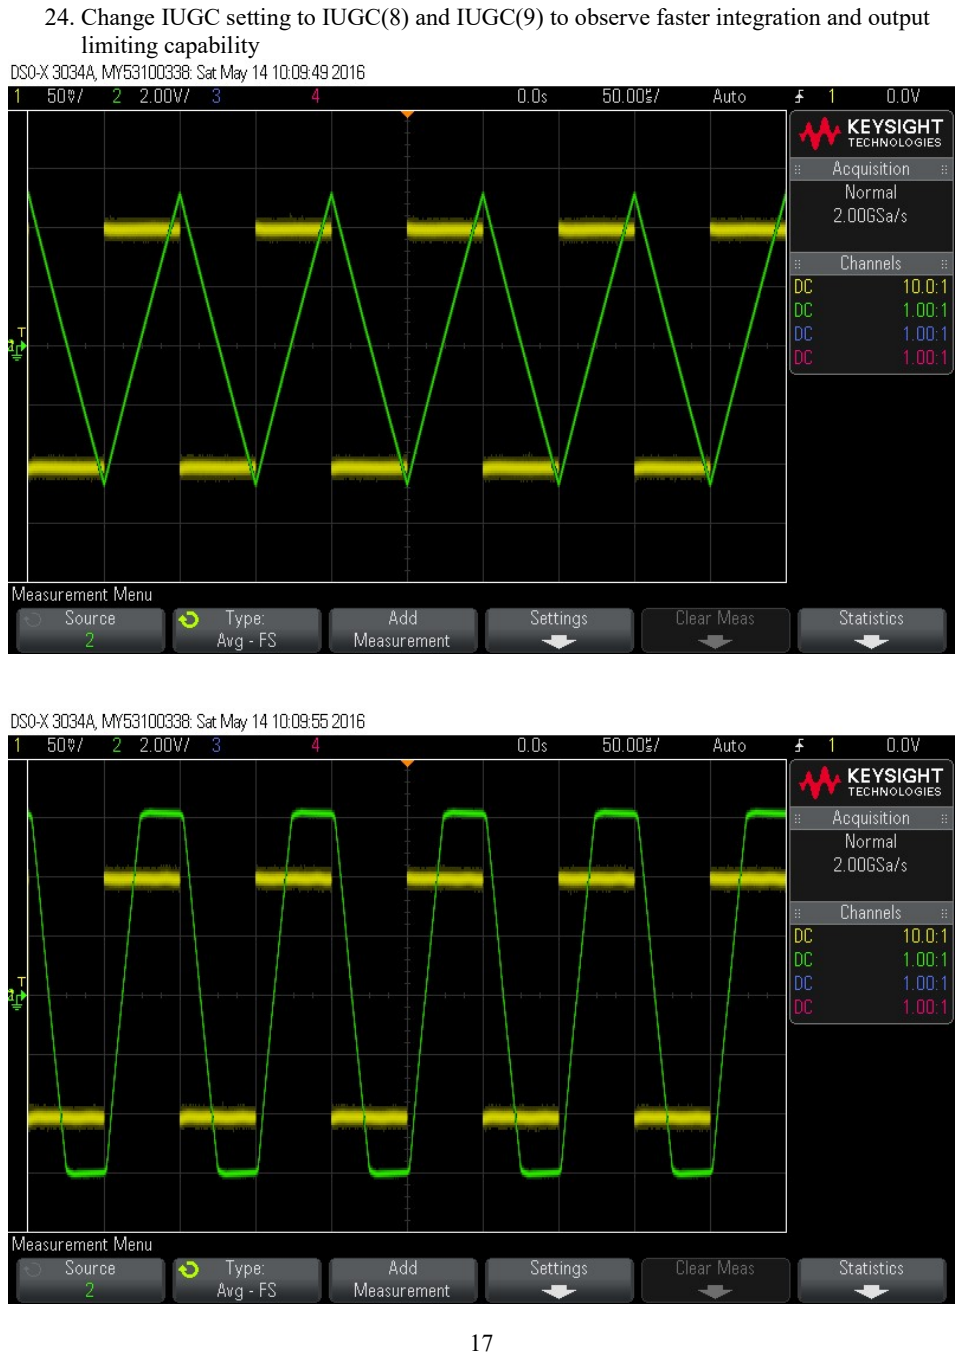
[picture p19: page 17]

17

### 24. Change IUGC setting to IUGC(8) and IUGC(9) to observe faster integration and output

limiting capability

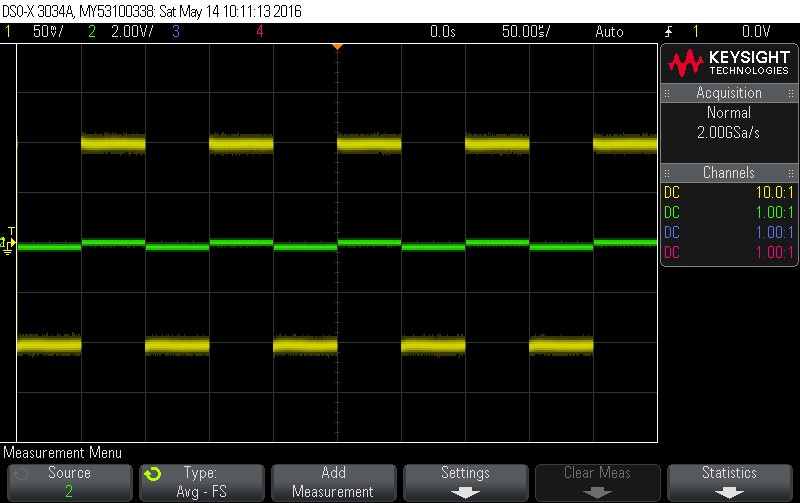
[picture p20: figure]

18

### 25. Set mode to LFGL with setting I_GAIN = Max, P_GAIN = 0, IUGC(9), LFGL(7) 26. Connect cable from OUT to IN2 (Self-Lock) 27. OUT_MON now should follow the reference square wave

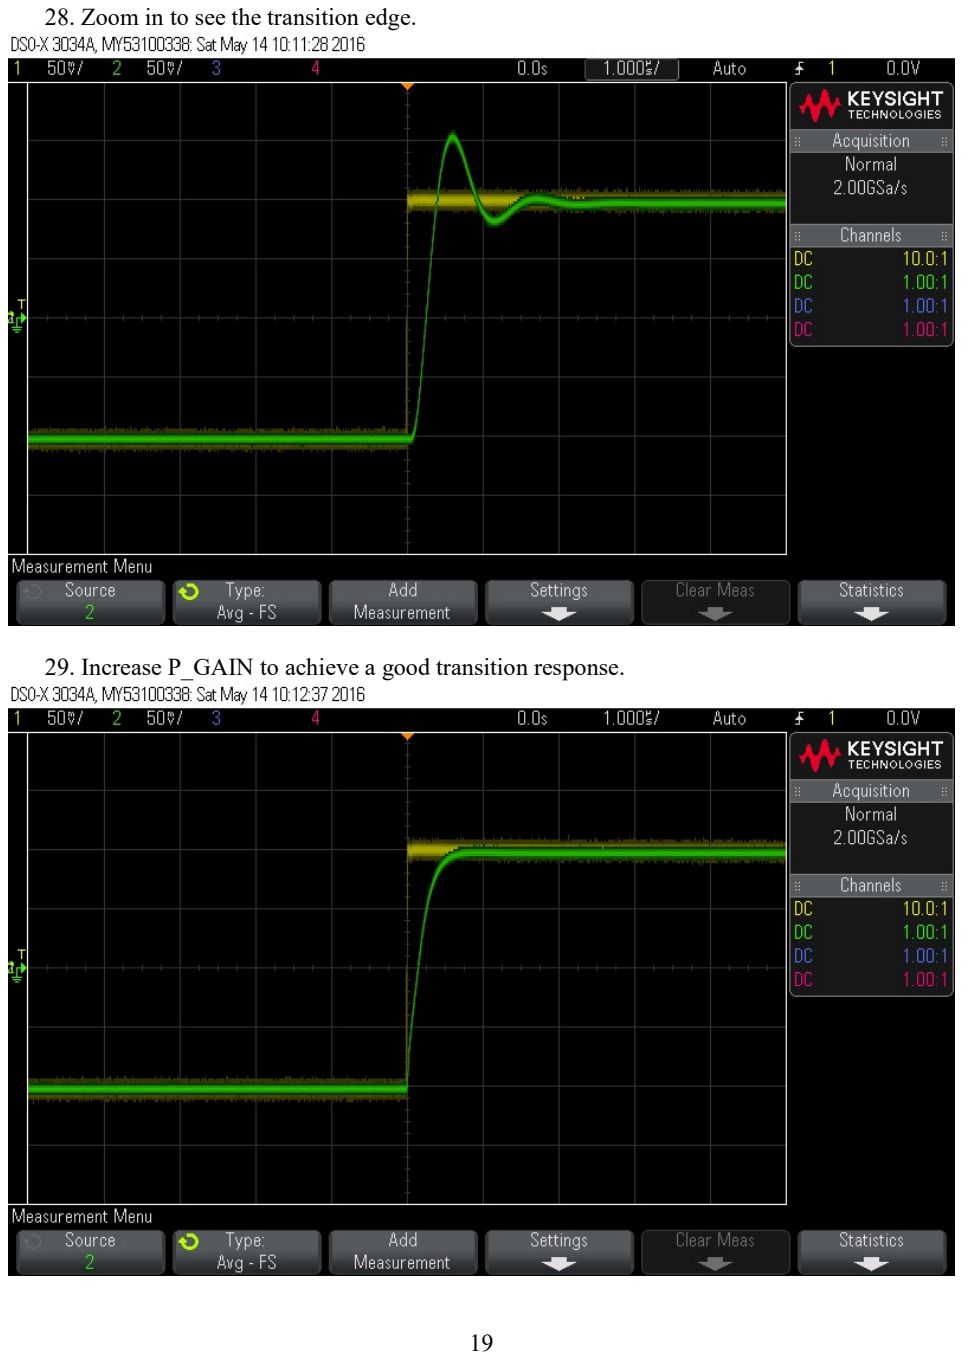
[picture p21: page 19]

19

28. Zoom in to see the transition edge.
29. Increase P_GAIN to achieve a good transition response.

20

Pin note
Potentiometer Pin
2
V
(CCW) 1------3 (CW)
SPDT Switch positions (key down):
DOWN (2—1), UP (2—3)
SP3T Switch positions (key down):
ON-ON-ON DP contact form (6Legs) (Part#7211P3YZQE)
DOWN (L2→L1, L5→L4), MID (L2→L3, L5→L4), UP (L2→L3, L5→L6) Upgrade from version 2.4.1
Version 2.5.2 can use enclosure of version 2.4.1 with a minor wiring modification. All 3 pins of control potentiometer knob #9 (see Front Panel) must be connected to 3-pin plug, which will be plugged to P_GAIN on the board. (PotPin1→PlugPin1, PotPin2→PlugPin2, PotPin3→PlugPin3)

21

Panel Cutout

### 3 BNCs: IN1, IN2, OUT

Diameter = 0.50 in.
Position:
From Left = 0.5+LeftSpace, +1.00, +1.00 in.
From Bottom = 0.375 in. + Standoff Length (Minimum 0.3 in.)

### 6 Trim pots: IN_OFFSET, LO_LIMIT, HI_LIMIT, ERR_DET, LO_DET, HI_DET

Diameter = 0.125 in.
Position:
From Left = LeftSpace+1.00, +1.00, +1.00, +0.25, +0.25, +0.25 in.
From Bottom = 0.25 in. + Standoff Length

### 4 Pots: FINE_OFFSET, OUT_OFFSET, GAIN, SWP_AMP

Hole Diameter = 0.37 in.
Key Diameter = 0.078 in., Offset 0.375 in.
Knob Diameter = 0.875 in.

### 4 BNC: IN_MON, ERR_MON, OUT_MON, EXT_SWP

Hole Diameter = 0.39 in.

### 2 Rotary Switches: PI_CORNER, LFGL_LEVEL

Hole Diameter = 0.25 in.
Key Diameter = 0.087 in., offset 0.256 in. Knob Diameter = 0.75 in

### 1 SPDT Toggle Switches: MON_IN1 1 SP3T Toggle Switch: UNLOCK/LFGL/LOCK

Diameter = 0.25 in.
Key Diameter = 0.094 in., offset 0.24 in.

### 1 LED Dual color R/G

Diameter = 0.19 in.
Front view pin down: Left = RED p-doped (anode)
Right = GREEN p-doped (anode)

### 1 Power Entry Module: 1 Rectangular 1.94 x 1.17 in. + 2 screw holes separated by 2.20in. 0.135 in. diameter

Front panel design files: PI_FPC.skp, PI_BPC.skp (SketchUp)

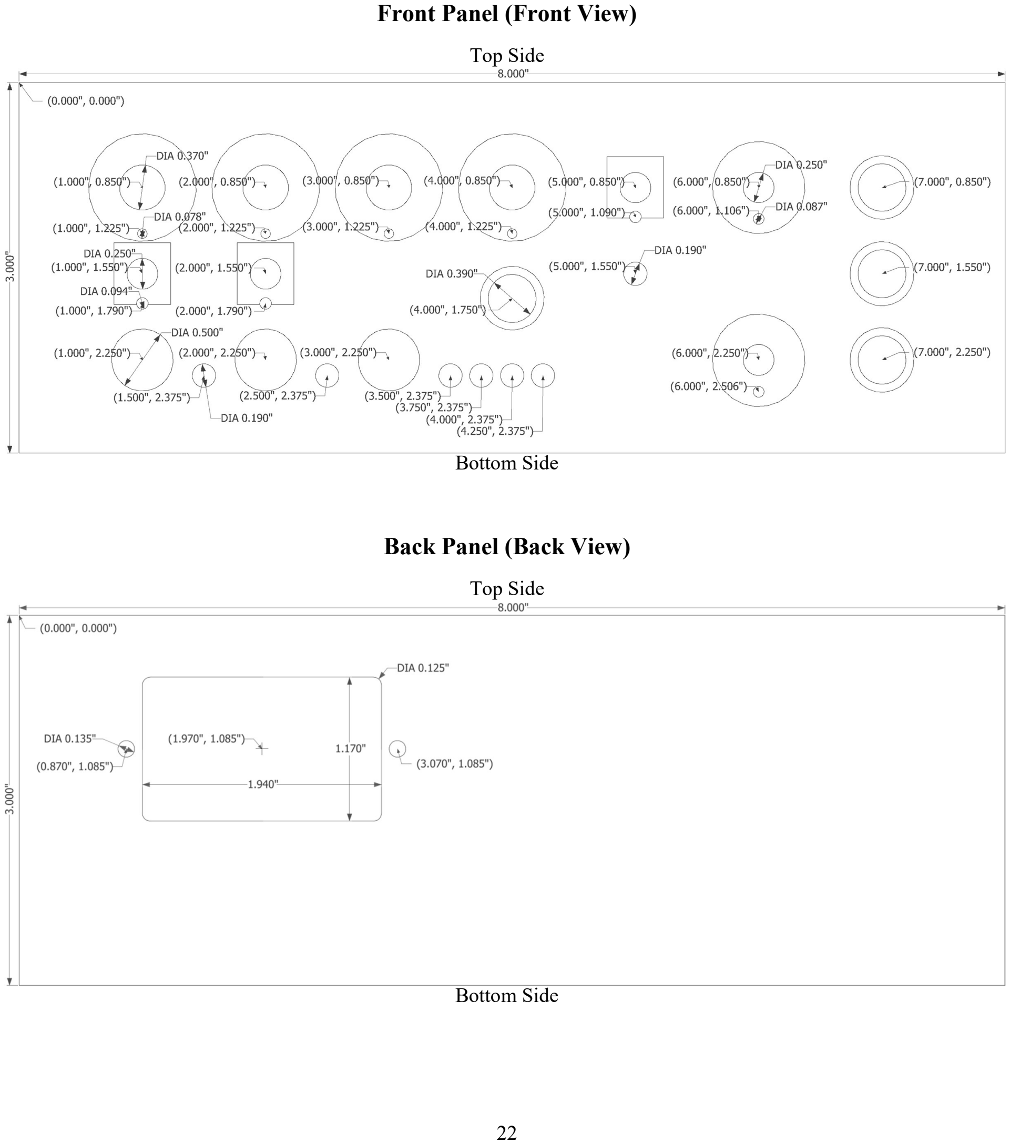
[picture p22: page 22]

22

### Front Panel (Front View)

Top Side

Bottom Side

### Back Panel (Back View)

Top Side

Bottom Side

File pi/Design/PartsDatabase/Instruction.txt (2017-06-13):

To use PI parts database:

1. In program MultiSim menu, Go to Options > Global preferences
2. Go to tab Paths
3. Specify User database path to the file UsrComp_S_PI.usr in this directory
4. Click OK to confirm changing user database.
5. Restart the program

Any change to parts in user database will be save to the file UsrComp_S_PI.usr in this directory

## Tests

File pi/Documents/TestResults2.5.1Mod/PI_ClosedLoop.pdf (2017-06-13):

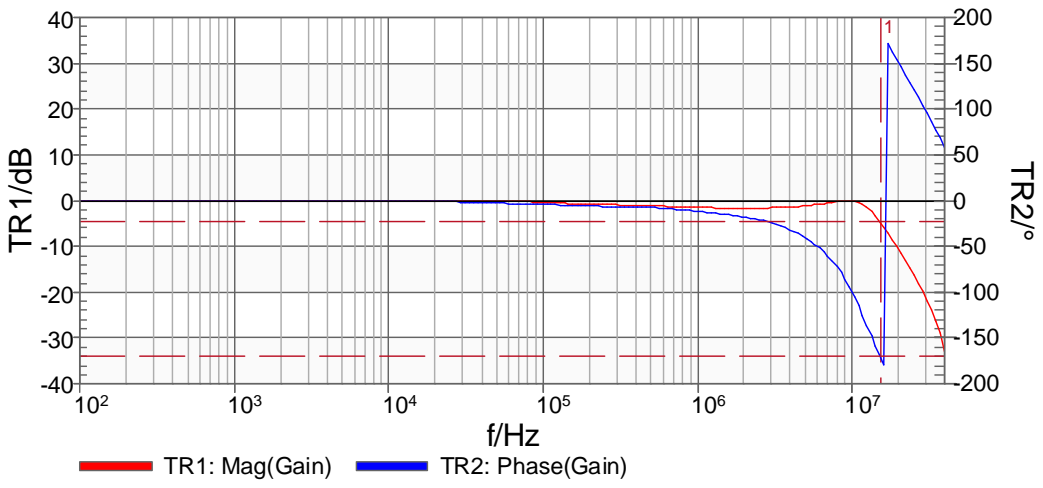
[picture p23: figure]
TR1: Mag(Gain); TR2: Phase(Gain)

Center Frequency : 20.000050 MH

Start Frequency :
Stop Frequency :

Span :
Sweep Mode :
Number of Points :

Level :
Attenuator CH1 :
Attenuator CH2 :
Receiver Bandwidth :

Reference Resistance :

100.000 Hz
40.000 MHz

39.999900 MH
Logarithmic
201

-22.00 dBm
20 dB
20 dB
10 Hz

50.00 Ohm

Gain | Mag(dB)
Gain | Phase(°)
Cursor 1 : | 15.344160 MHz | -4.687 dB | -170.000 °
Cursor 2 :
Delta :

Sweep

Configuration

Measurement

Cursor

Calibration
Probe :
User :
On | -
- - Device Settings

DUT delay :
Impedance CH1 :
Impedance CH2 :
Switch CH1 :
Switch CH2 :
| 0.00 s 1 MOhm 1 MOhm Internal CH2
Frequency | Trace 1 | Trace 2

TR1 :
TR2 :
Measurement | Format
Gain | Imp.
Trace | Comment I_GAIN=20dB, IUGC(10)=1MHz, LFGL(5)=40dB, P_GAIN=15dB

# Frequency Sweep

2014-11-25 4:39:51 PM | PI_ClosedLoop.bodex | 1 / 1 | Bode 100 [SerNo: LG278C]

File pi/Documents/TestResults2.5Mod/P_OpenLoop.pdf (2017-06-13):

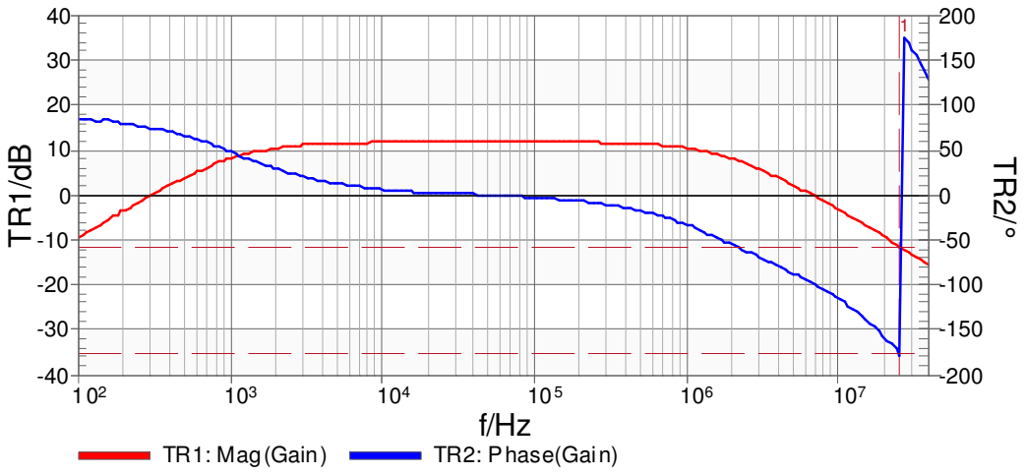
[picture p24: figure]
TR1: Mag(Gain); TR2: Phase(Gain)

Center Frequency : 20.000050 MH

Start Frequency :
Stop Frequency :

Span :
Sweep Mode :
Number of Points :

Level :
Attenuator CH1 :
Attenuator CH2 :
Receiver Bandwidth :

Reference Resistance :

100.000 Hz
40.000 MHz

39.999900 MH
Logarithmic
201

-10.00 dBm
20 dB
20 dB
300 Hz

50.00 Ohm

Gain | Mag(dB)
Gain | Phase(°)
Cursor 1 : | 25.031114 MHz | -11.402 dB | -176.000 °
Cursor 2 :
Delta :

Sweep

Configuration

Measurement

Cursor

Calibration
Probe :
User :
On | -

Device Settings
DUT delay :
Impedance CH1 :
Impedance CH2 :
Switch CH1 :
Switch CH2 :
| 0.00 s 1 MOhm 1 MOhm Internal CH2
Frequency | Trace 1 | Trace 2

TR1 :
TR2 :
Measurement | Format
Gain | Imp.
Trace | Comment IGAIN=-60dB, PGAIN=12dB

# Frequency Sweep

2014-10-09 6:00:15 PM | P_OpenLoop.bodex | 1 / 1 | Bode 100 [SerNo: LG278C]

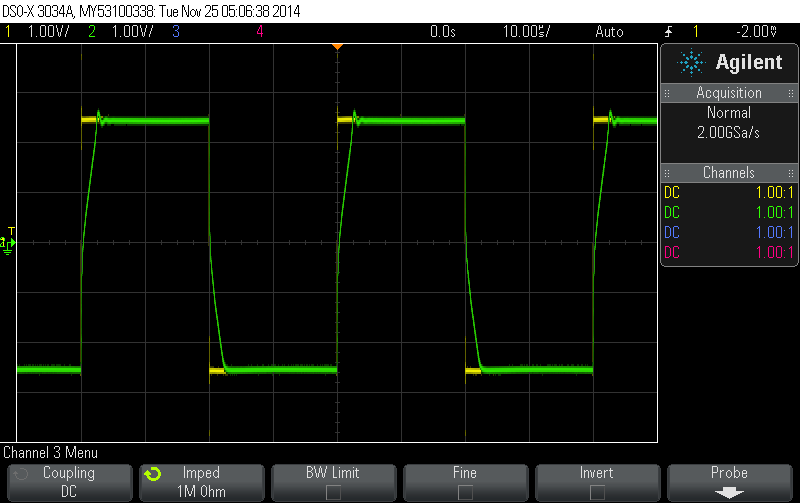
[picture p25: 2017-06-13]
pi/Documents/TestResults2.5.1Mod/scope_9.png

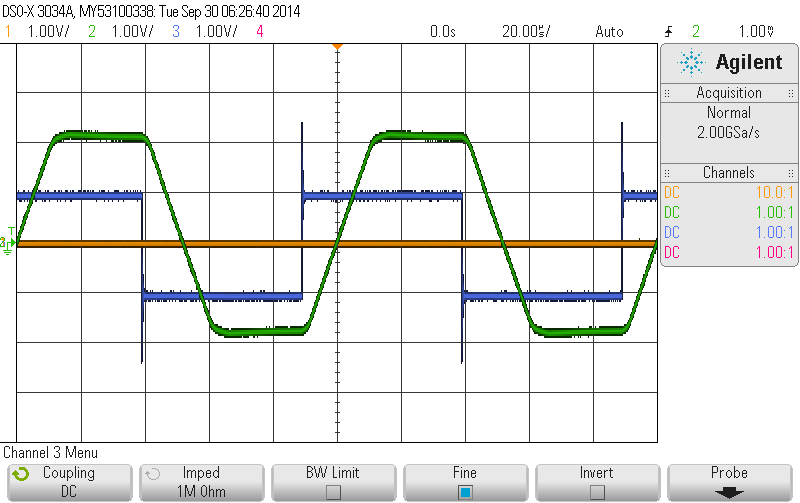
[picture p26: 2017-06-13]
pi/Documents/TestResults2.5Mod/LimitedIntegrator.png

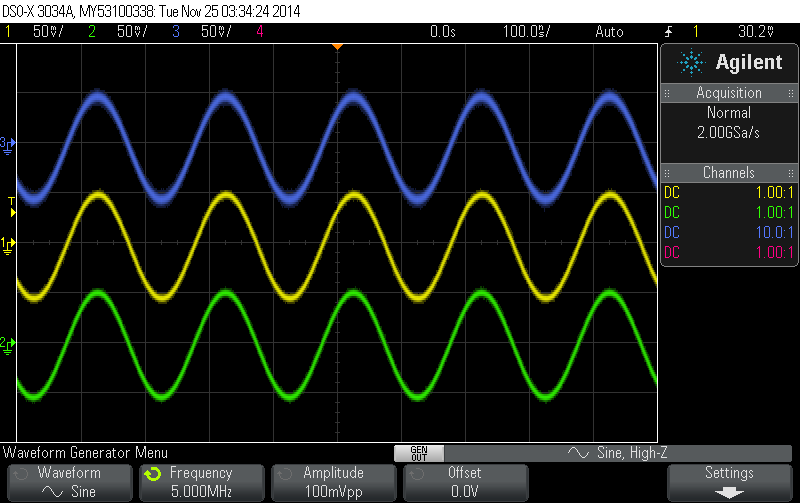
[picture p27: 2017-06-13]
pi/Documents/TestResults2.5.1Mod/scope_5.png

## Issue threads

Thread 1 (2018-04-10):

### ISSUE TITLE
PI_NC_Drill.drl file is not included in analog-pi/pi/Design/Gerber/  folder

### ISSUE THREAD

**Issue by JackRoten** [JQIamo/analog-pi#1]
I am building the PI Lockbox, currently I am in the stages of building the PCBs with a PCB company. There is one file that looks like it is missing from the pi/Design/Gerber/  folder that we will need to fully build these PCBs. LayerMap.txt lists PI_NC_Drill.drl as a file for the PI PCB, but it seems to be missing from the Gerber folder.

**Comment by restelli** [comment]
@JackRoten thanks for signaling the problem: there must have clearly been issues during the generation of the artwork files. I will look into the issue and get back on this as soon as possible. In the mean time please put the PCB fabrication in hold.

**Comment by restelli** [comment]
I believe that the gerber file for fabrication are in the "fab" directory therefore they should be found here: 
analog-pi/fab/pi_v2.5.3_CAD/
The content of pi/Design/Gerber/ is likely an outdated copy of the artwork. I will go through the project and issue a commit that clarifies the situation. In the main time I suggest to keep the fabrication on hold.

**Comment by restelli** [comment]
Closed with commit:  b25263b

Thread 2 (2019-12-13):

### ISSUE TITLE
Proportional VGA calibration

### ISSUE THREAD

**Issue by xiongjunwen44** [JQIamo/analog-pi#2]
Hi, 

Our group bought ~10 JQI pi controller v2.5.3 and I'm trying to go through the Initial Calibrations and Tests on p. 14 of the manual. However, I encounter difficulties in the Proportional VGA calibration part.

For step 11 and 12, U9-Pin10 and POT2 are inaccessible once all the front panel controls are connected to the board. I tried connecting the PCB with U9 and POT2 to the board with cables instead, which makes U9 and POT2 accessible. However, the cable connections are not quite reliable given the number of Molex connectors I need to make. Thus, I'm wondering if there's an easier way to access U9 and POT2 once everything is assembled. 

Thanks a lot!

**Comment by dsbarker** [comment]
Hi Junwen,

This is a known issue with the snap-together PCB assembly of the board. Because the documentation was written before the snap-together assembly was developed, the documentation doesn't mention the difficulty in setting up the snap-together boards.

We have some boxes (for older versions of the PCBs) that use ribbon cables to make all the necessary connections so that U9 and POT2 are accessible. We usually install the analog-pi PCB into one of the old boxes for calibration and then move it into a new box with the snap-together components. Of course, that solution has already occurred to you and, without an assembled box, it's not easy to get working.

We may have a spare calibration box that we can send you. I'm not at JQI today, but I can check for one when I'm there tomorrow.

Daniel

**Comment by xiongjunwen44** [comment]
Thanks a lot, Daniel! If there's a spare calibration box available, it
would be the easiest solution thus far I think!

If not, could you maybe send me a picture of the calibration box and the
part numbers for the ribbon cables and connectors if you happen to have
them? That way, it might be easier for me to build one myself. I've been
searching for connectors that match the Molex housings and headers but
haven't found any yet. Thanks so much for your help!

Best,
Junwen

**Comment by dsbarker** [comment]
I sent you an e-mail with pictures of the calibration box and some suggestions.

**Comment by dsbarker** [comment]
Closed with commit https://github.com/JQIamo/analog-pi/commit/e8bcea54c6d4ed05e0ef3ee88577ae0c8bdc9aef

I've added windows in the shield PCB to allow access to the potentiometers and U9.

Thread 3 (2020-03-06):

### ISSUE TITLE
INPUT OFFSET en/dis jumper on the board

### ISSUE THREAD

**Issue by xiongjunwen44** [JQIamo/analog-pi#3]
Hi,

Thanks a lot for the help with the connectors last time! Sorry I have another question. So, we ordered 10 jqi lockboxes in total. When I was building them, 3 of them broke. 

For the first one, the OUTPUT OFFSET cannot adjust the OUTPUT MONITOR at the unlock mode. However, the HIGH LIMIT is able to decrease the OUTPUT MONITOR readings. For the second one, the OUTPUT OFFSET again could not adjust the OUTPUT MONITOR at the unlock mode. And, the HIGH LIMIT cannot decrease the OUTPUT MONITOR readings either. For the first two boards, the boards get really hot when plugged in. 

For the third one, most things are correct. However, at the Proportional VGA calibration step, the POT1 (P_VGA_IN_TRIM) cannot adjust the output of VGA(U9-PIN10). And for the square wave reference test, increasing P_GAIN cannot smooth the transition edge. 

We think the three boards broke because the jumper for INPUT OFFSET was not connected initially (which is not indicated in the manual!) or was badly made. To fix the boards, we try measuring the voltage at the 4 regulators, which function properly as the PI_Schematic indicates. Sorry for asking. But, do you have any ideas how we might be able to fix it? And whether the jumper is really the problem?
![IMG_7460](https://user-images.githubusercontent.com/32970730/74977718-1d71d300-53e0-11ea-9c8f-a3dbed5e1c13.jpg)

Best,
Junwen

**Comment by dsbarker** [comment]
Hi Junwen,

The high and low limits must be set such that the output offset is between them at all times. Otherwise the boards will behave strangely. I would suggest powering off both of the first two boards, maximizing/minimizing the high/low limits, setting the output offset pot to the middle of it's range (5, 0 if you're using an indicating dial), repowering the board and trying the adjustments again.

The offset jumper is another feature that was added after the manual was written. The solder bridge in the picture should work fine. Digikey also sells jumpers that you can use (I'll send the part number later).

I'm not sure what's wrong with the other board, but I'll think about it and try to get back to you tomorrow.

**Comment by dsbarker** [comment]
If you don't want to solder-bridge the input offset jumper, you can use S3404-ND. I'm not sure that failing to place the input offset jumper would cause the PCBs to fail.

The regulators can source quite a bit of current. They'll probably still work even if an IC is dead. Is any one of the regulators particularly hot?

For all the broken boards, please check if any of the op amp ICs are very hot. If any IC is hot enough to cause pain when you touch it, then it probably needs to be replaced. I use a reworking station (e.g. the BK4050 from circuit specialists) to remove and place multipin components. You'll need some solder paste as well.

For the third board, since the VGA input trim is not working, I would guess that either U8 or U9 is dead. What is the voltage at U9, pin 10? Does the voltage change when you go to locked mode (you'll need to test this with a scope since there's no P gain at DC)? Does the VGA output trim do anything?

**Comment by xiongjunwen44** [comment]
Hi Daniel,

Thanks a lot for the reply! I think for the first two boards, U27 and U29 are not functioning properly. When U27 IN+ is set to around 6V, its OUT is -12V. There's a +20V increase across the D8B and U27 IN- was set to around 8V. The current is flowing backwards across the diode. For U29, when IN+ is set to -6V, U29 OUT sets U29 IN- to +10V instead. Both U29 and U27 are powered properly. 

For the third board, I think the main issue is that R83 is missing from the board. The voltage range for POT10 is thus from -5V to -5V and the proportional gain cannot actually be increased. 

I might try to find the soldering station you recommend, put on R83 and replace U27 and U29. I'll also order the jumper connectors you recommend. Do you have a better idea why U27 and U29 are not functioning properly? Are they broken because some other part of the circuits? Or they're broken because the Lim- is higher than Lim+ when they were first powered? Hope to find a way to avoid the issue.

Best,
Junwen

**Comment by dsbarker** [comment]
I don't think anyone has ever tracked down the exact limit settings that are needed to damage the board. With luck, we'll get to the bottom of it this time.

I took a look at the output limiting section of the schematic. Based on your description of the problem on the first two boards, U27 is probably fine. The operation that you describe is normal when OUT_LO_LIMIT is set higher than OUT_HI_LIMIT. The differential voltage across U27's inputs is within spec. 

It does sound like U29 is malfunctioning, since it should servo its IN- to match IN+... A 2 V drop across R91 is quite large. It suggests that U28's IN+ is not acting as a high impedance. If U28 OUT is at 8 V, then a large current is flowing from U29 through D6A/D6B into U28. I'm not sure how such a situation would develop, but it could be enough to damage both U28 and U29.

Things to check:
1. Is R91 a 10 kOhm resistor as it should be?
2. Is U29 or U28 hot (enough to burn you or make a damp q-tip sizzle)?
3. What is the voltage at U17 OUT (pin 6)?
4. What is the output offset (U22, pin 6)?

I would guess that replacing U28, U29, and (perhaps) D6 will fix the problem. Provided that you set LIM+ > OUT_OFFSET > LIM- before repowering the boards.

**Comment by xiongjunwen44** [comment]
Thanks a lot for the reply! I have replaced U28 and U29 and the board is working right now. I think I'll be more cautious setting the high and low limits before turning on the board next time.

**Comment by dsbarker** [comment]
After discussing with other JQI electronics people, it seems like the problem is due to the limits being allowed to go all the way to the supply rails. If there were voltage-limiting resistors in line with POT12 and POT13, then the problem could be resolved. The LM7171 op amp (U28 and U29) can only source/sink 100 mA. If LIM- = 12 V and LIM+ = -12 V then the two op amps will sink too much current and damage themselves.

If LIM-/LIM+ were limited to +/- 6 V by inserting limiting resistors, then I think the bug would be resolved. Something to think about for future updates (or hacking into the current board in future production runs).

**For people setting up new boards:** I recommend using a multimeter to ensure that POT12, pin 2 is shorted to the 12 V rail (and that POT13, pin 2 is shorted to the -12 V rail) before powering up the the PI board. You'll probably need to do this test before installing the PCB into the box.

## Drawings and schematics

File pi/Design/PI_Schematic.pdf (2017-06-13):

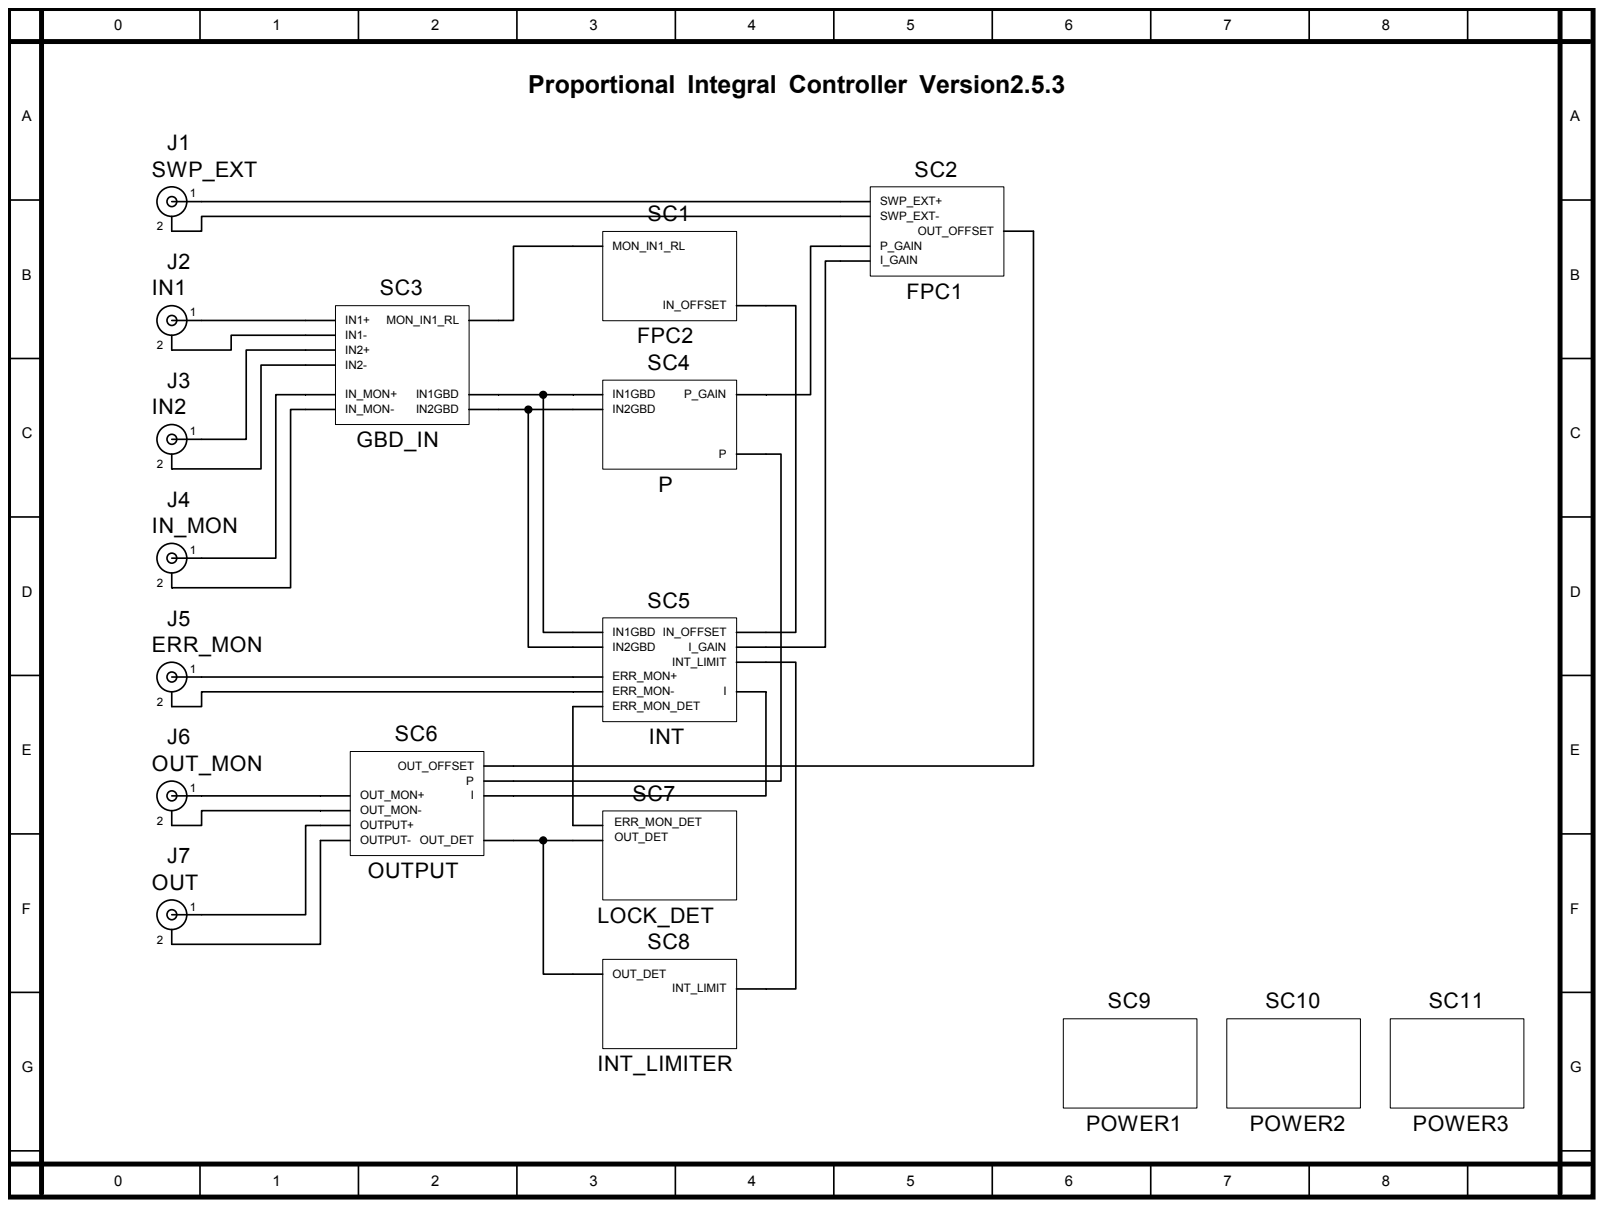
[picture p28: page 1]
J5 ERR_MON; J6 OUT_MON; J7 OUT; J1 SWP_EXT; J4 IN_MON; GBD_IN; IN1GBD; IN_MON-; IN2GBD; IN_MON+; MON_IN1_RL; IN1GBD IN2GBD; P_GAIN; INT; INT_LIMIT; I_GAIN; IN_OFFSET; ERR_MON+ ERR_MON- ERR_MON_DET; INT_LIMITER; OUT_DET; OUTPUT; OUTPUT+ OUTPUT-; OUT_MON+ OUT_MON-; OUT_OFFSET OUT_DET; LOCK_DET; ERR_MON_DET OUT_DET; FPC1; SWP_EXT+ SWP_EXT- P_GAINOUT_OFFSET; FPC2; POWER1; POWER2; POWER3

Proportional Integral Controller Version2.5.3

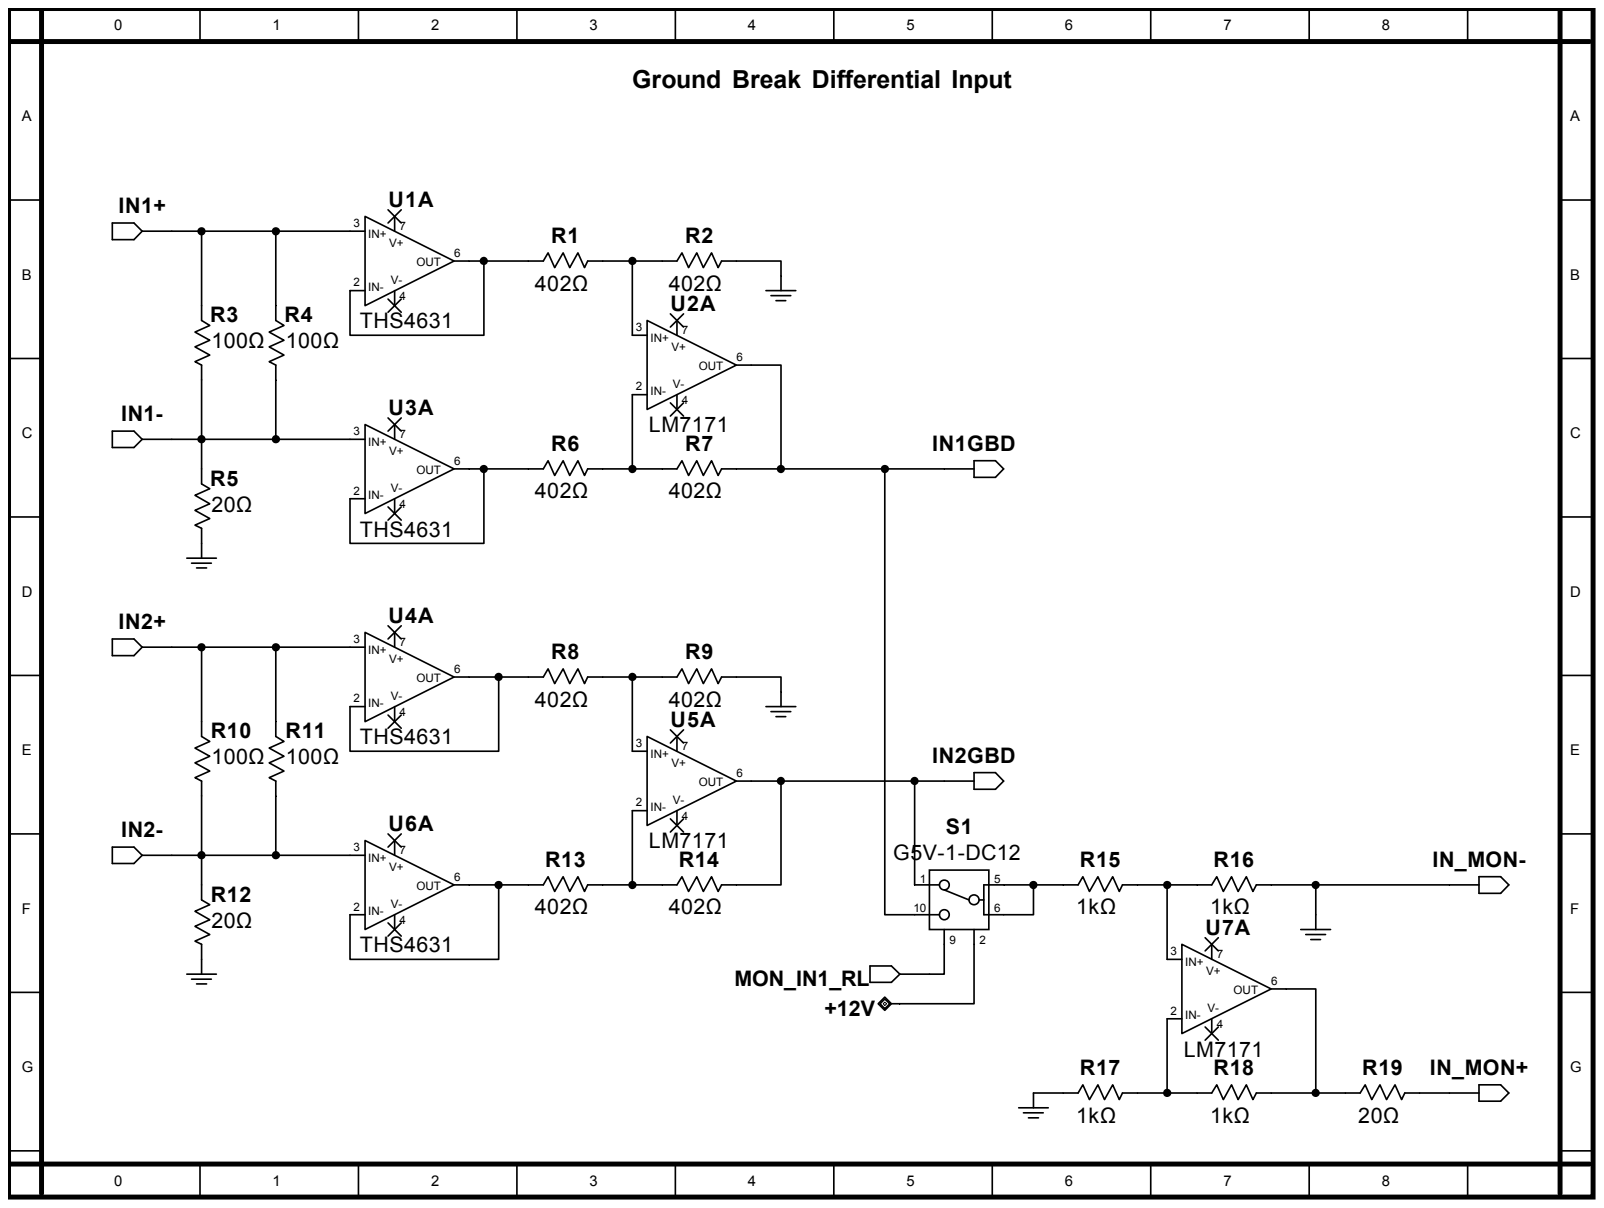
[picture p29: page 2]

Ground Break Differential Input

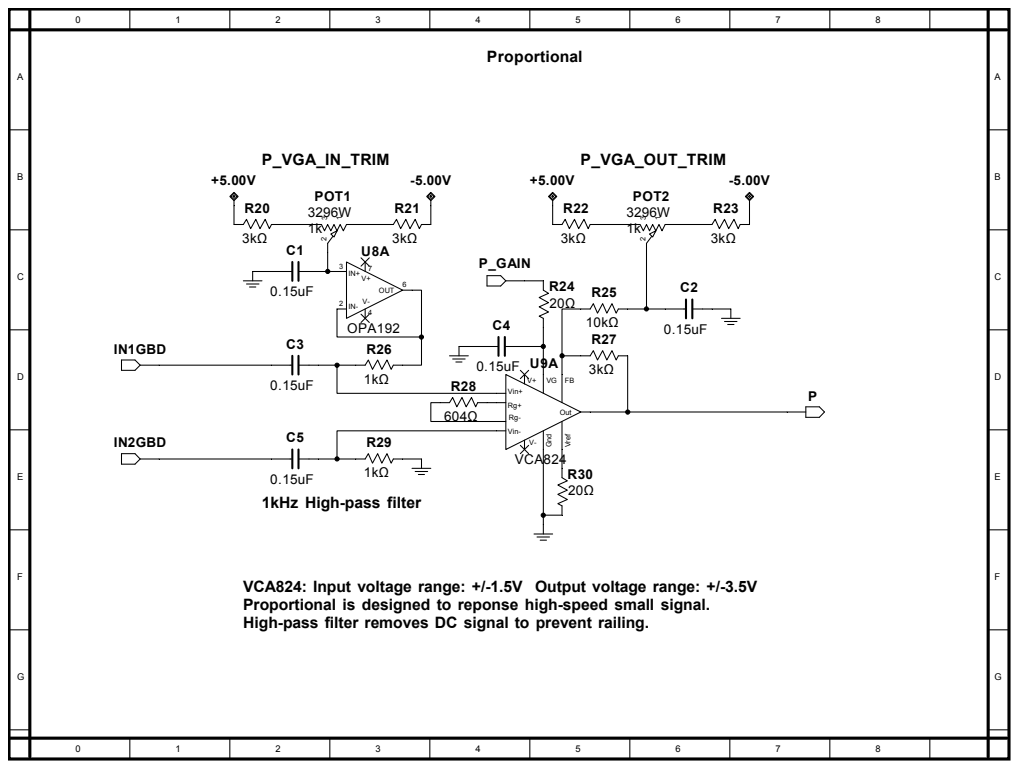
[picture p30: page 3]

VCA824: Input voltage range: +/-1.5V Output voltage range: +/-3.5V
Proportional is designed to reponse high-speed small signal.
High-pass filter removes DC signal to prevent railing.

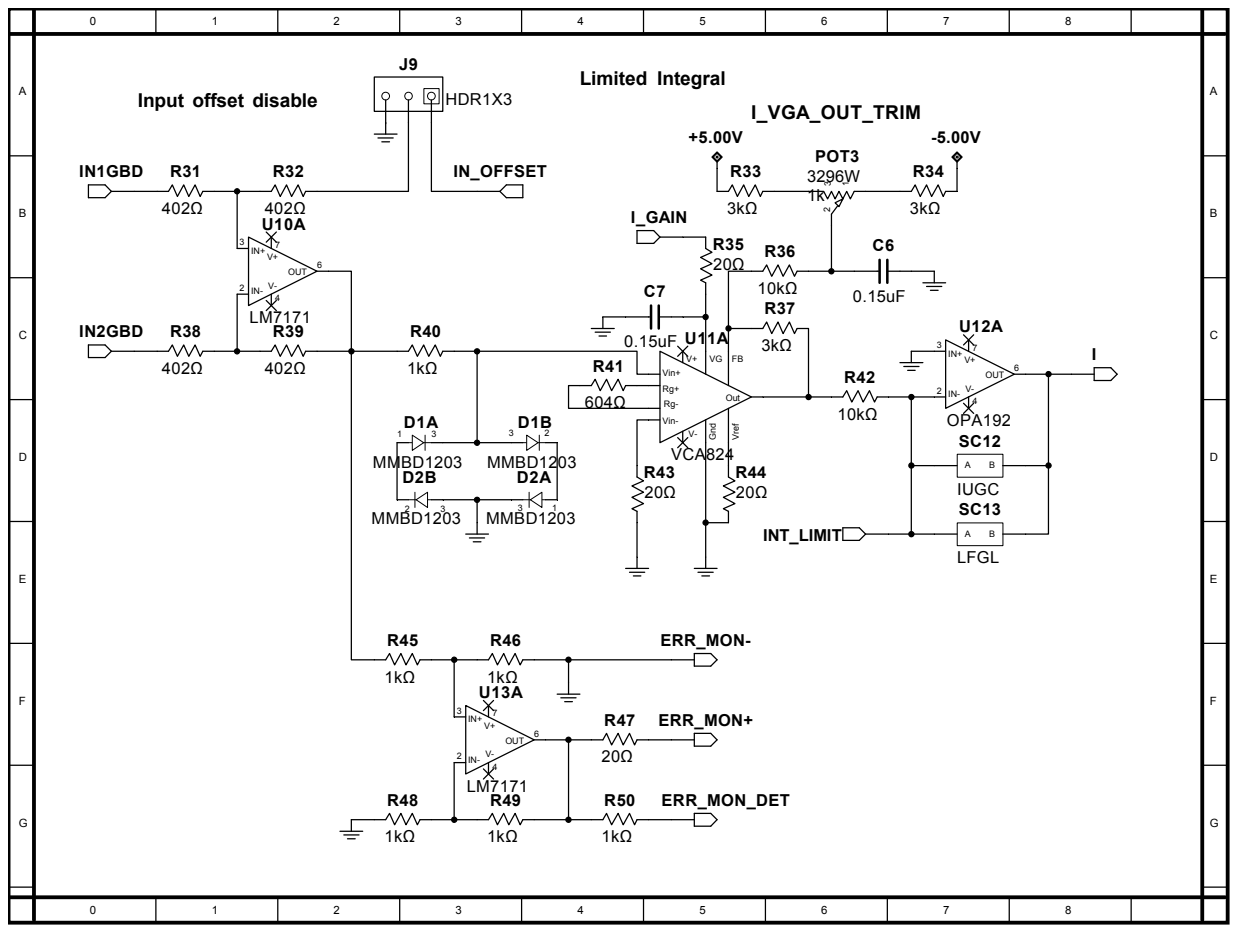
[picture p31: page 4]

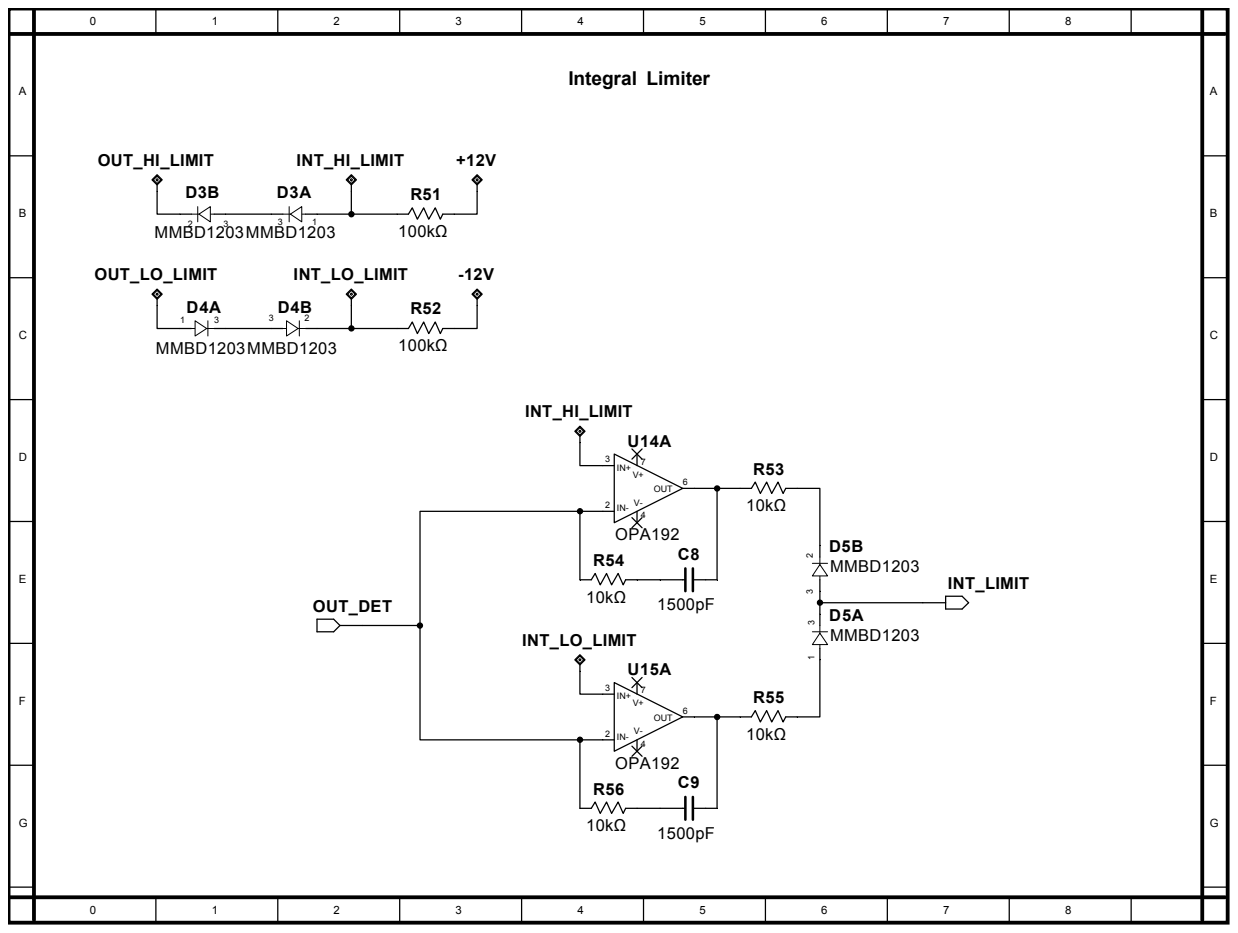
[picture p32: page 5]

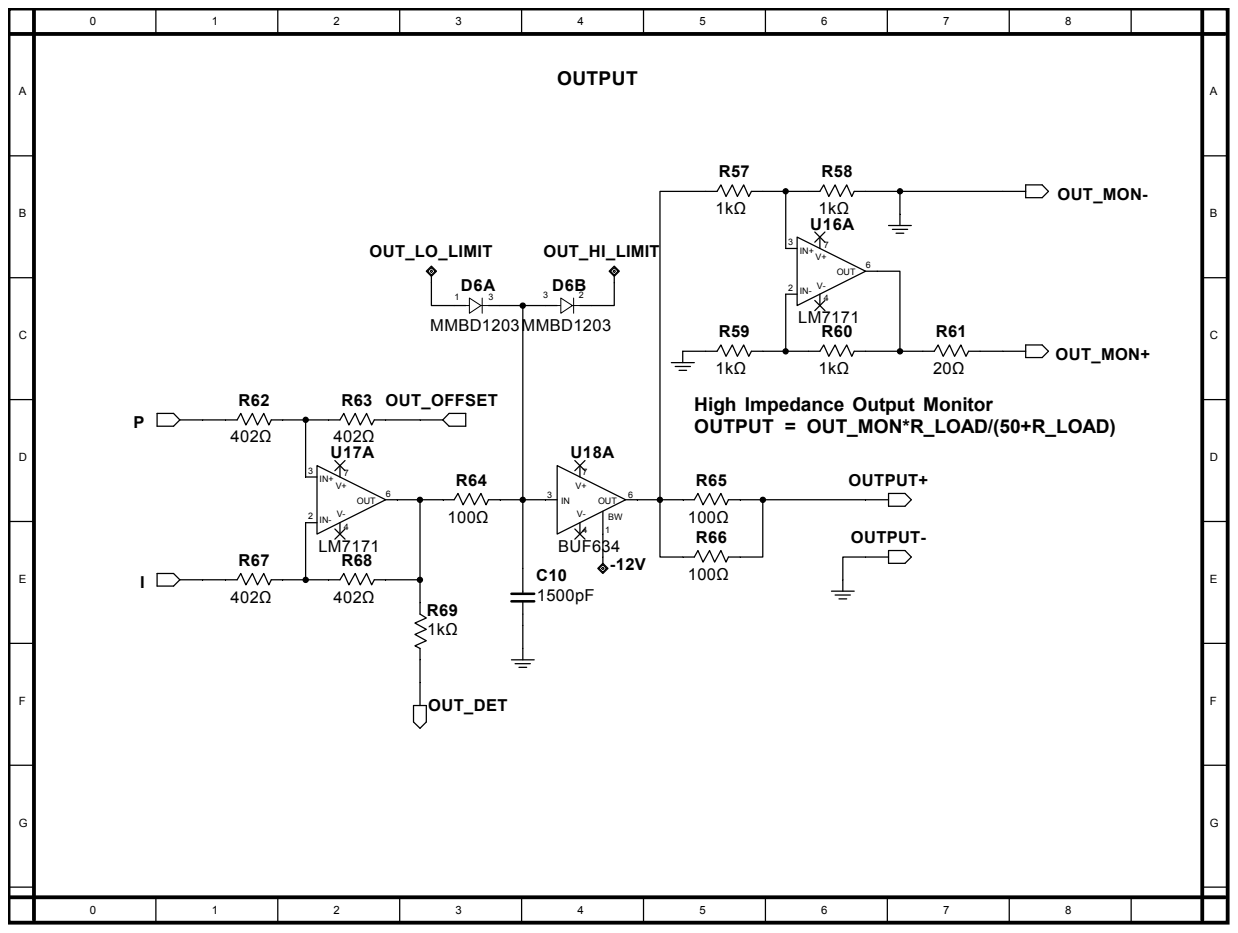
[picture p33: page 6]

High Impedance Output Monitor
OUTPUT = OUT_MON*R_LOAD/(50+R_LOAD)

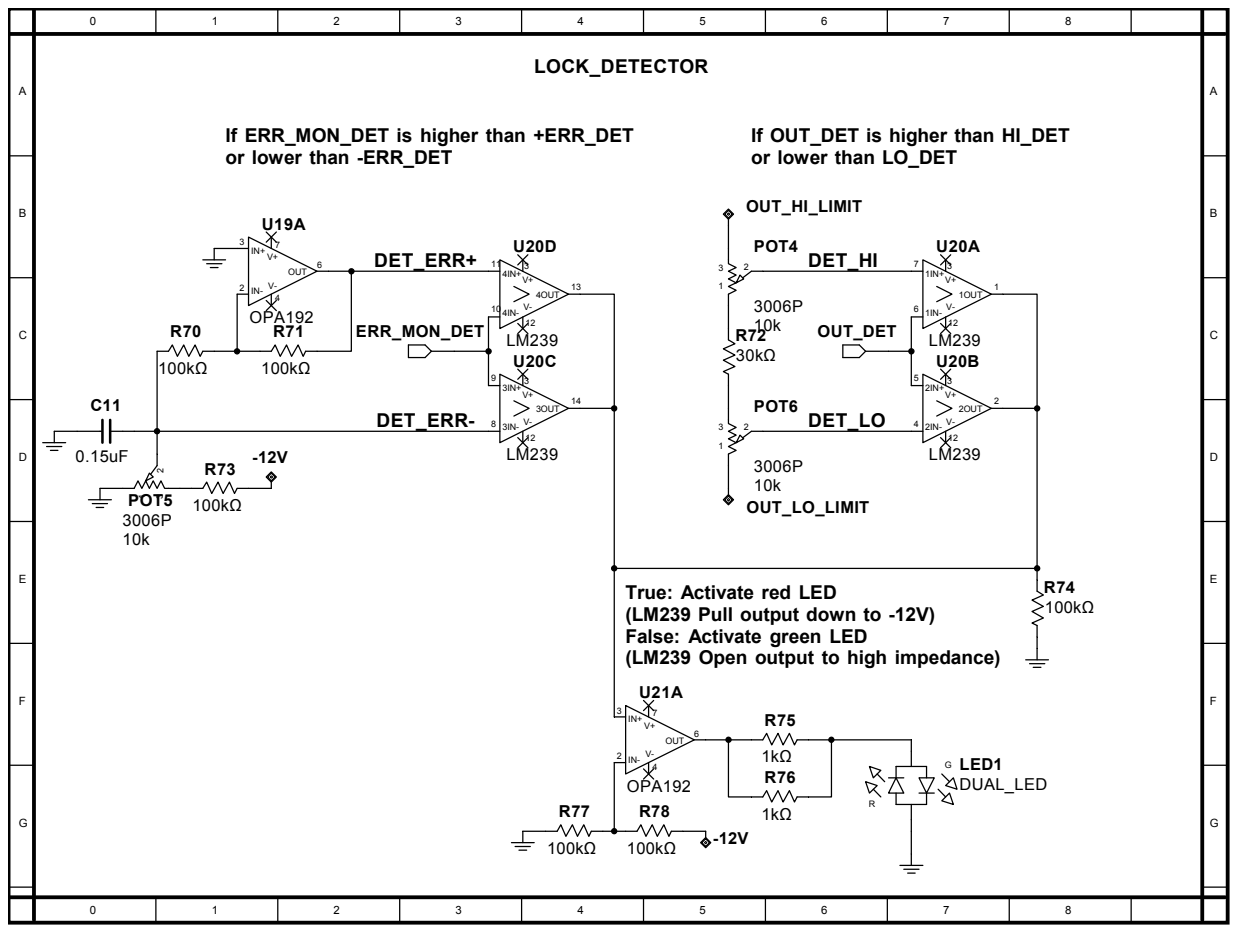
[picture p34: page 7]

If ERR_MON_DET is higher than +ERR_DET
or lower than -ERR_DET

If OUT_DET is higher than HI_DET
or lower than LO_DET

True: Activate red LED
(LM239 Pull output down to -12V)
False: Activate green LED
(LM239 Open output to high impedance)

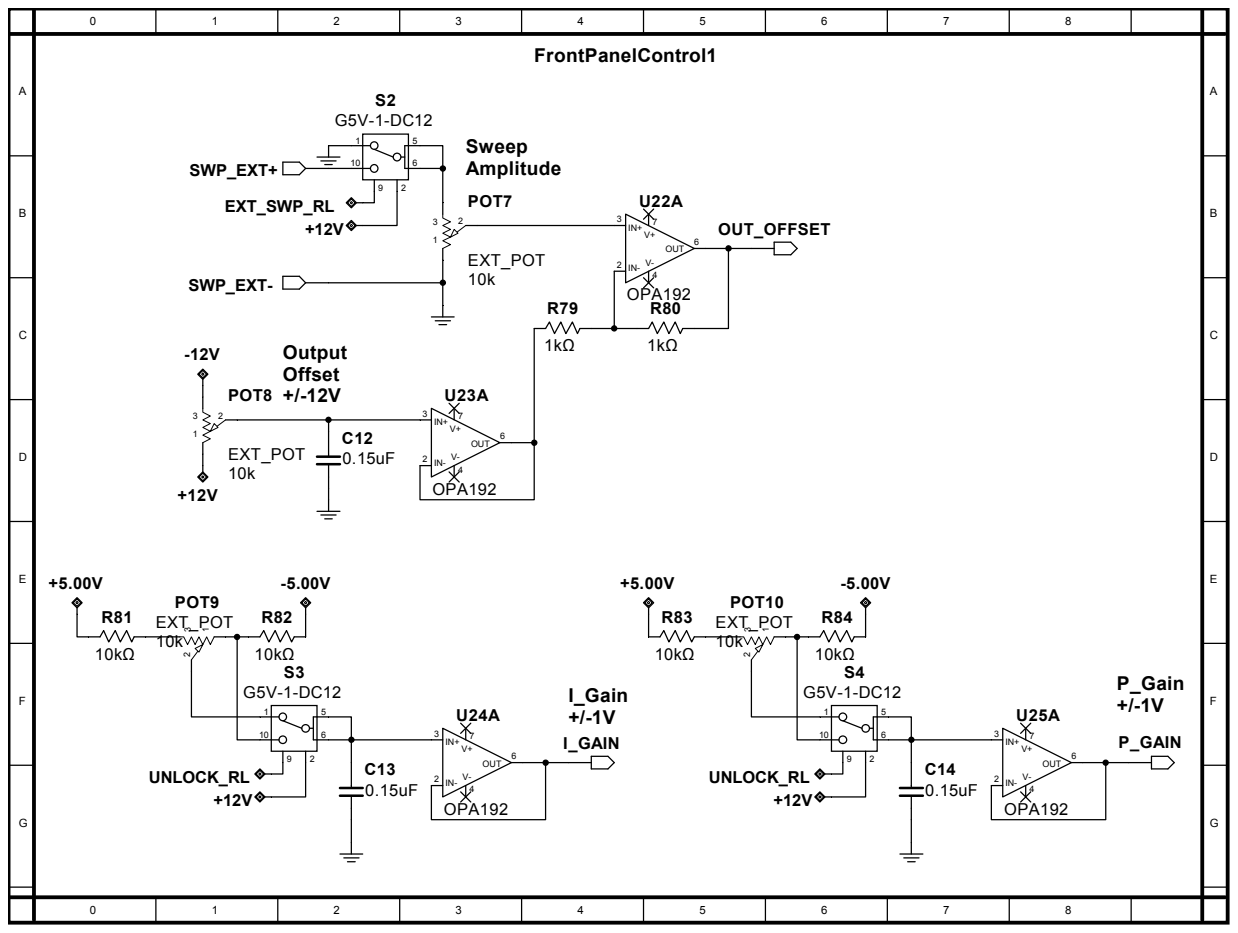
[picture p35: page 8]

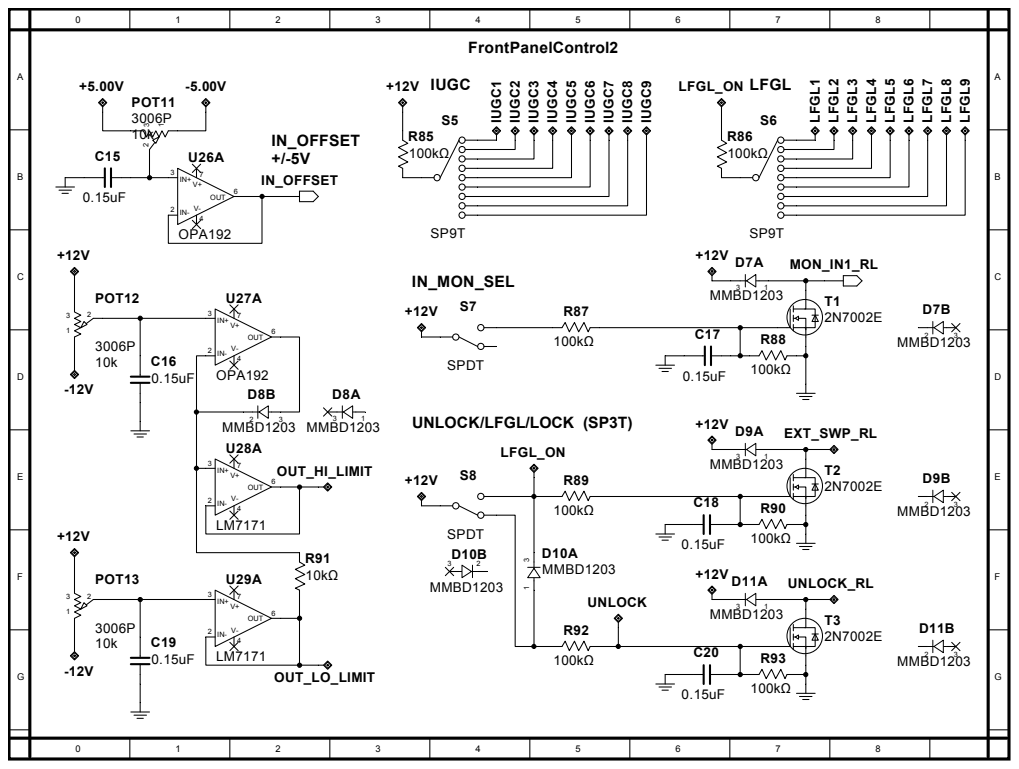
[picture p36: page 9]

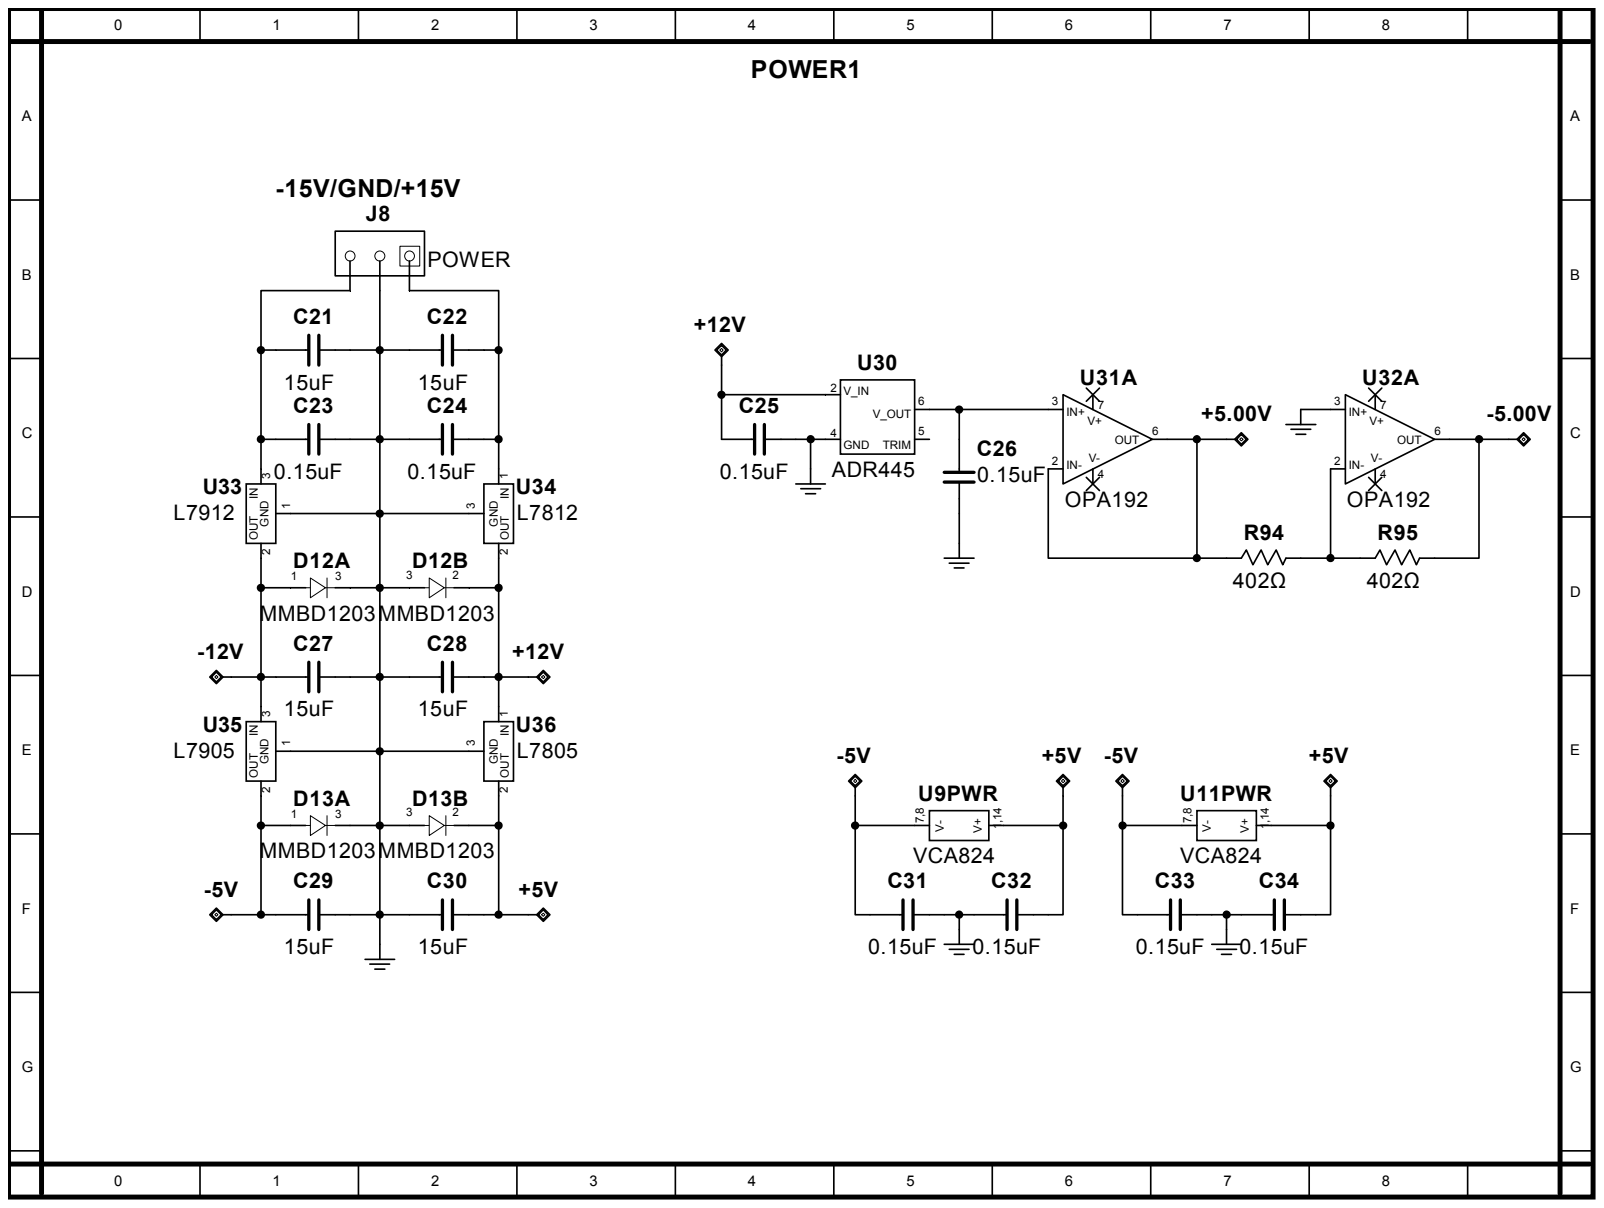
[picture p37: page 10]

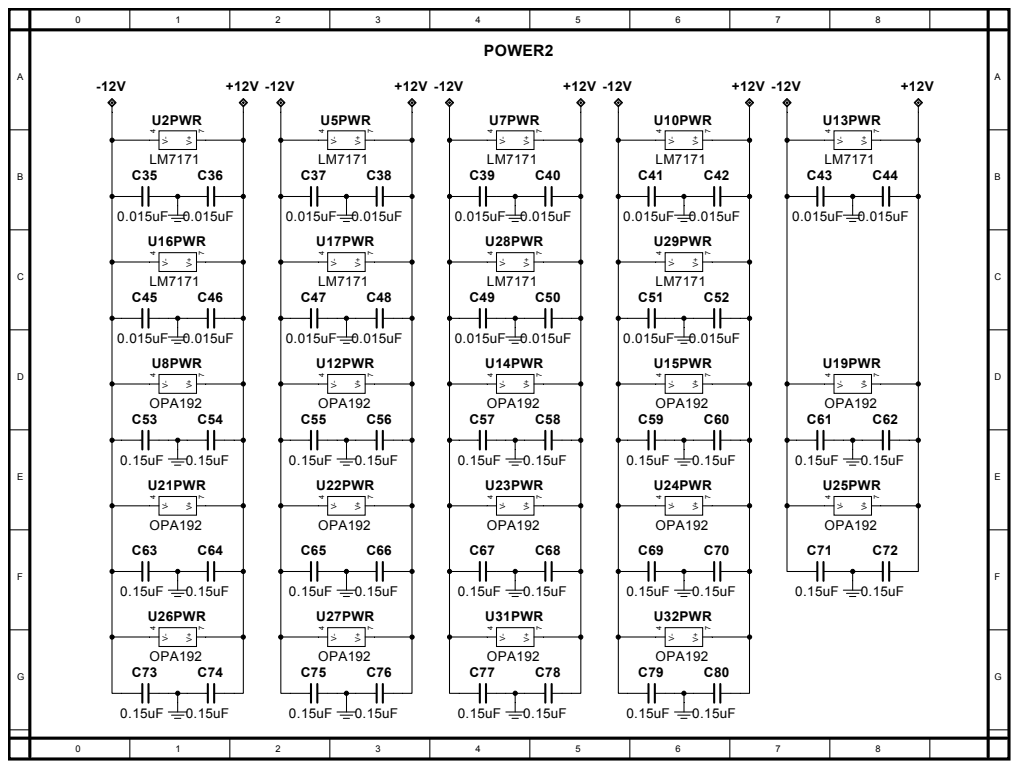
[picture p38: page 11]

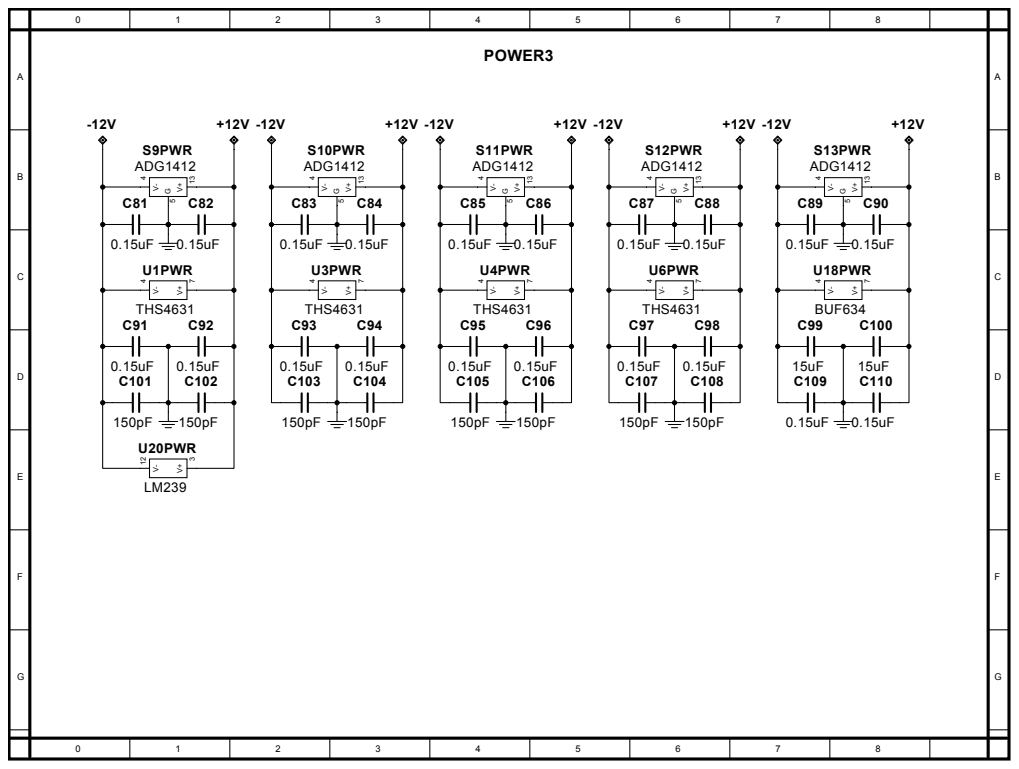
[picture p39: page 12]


Integral Unity Gain Cutoff
IUGC5 0.015uF 3.4kHz -> 10kHz

Switch de-bounce capacitors


Low Frequency Gain Limit

100kΩ | 100kΩ | 100kΩ | 100kΩ | LFGL8 100kΩ | LFGL9 100kΩ | 100kΩ

Switch de-bounce capacitors

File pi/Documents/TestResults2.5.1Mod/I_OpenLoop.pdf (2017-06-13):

# Frequency Sweep

100.000 Hz 40.000 MHz; 39.999900 MH Logarithmic 201; -22.00 dBm 20 dB 20 dB 10 Hz; 50.00 Ohm; Gain; Mag(dB); Phase(°); Cursor 1 :; 1.032467 MHz; Cursor 2 : Delta :; Cursor; Calibration Probe : User :; - - Device Settings; DUT delay : Impedance CH1 : Impedance CH2 : Switch CH1 : Switch CH2 :; 0.00 s 1 MOhm 1 MOhm Internal CH2; Frequency; Trace 1; Trace 2; Measurement; Format; Imp.; Trace; Comment; I_GAIN=20dB, IUGC(10)=1MHz, LFGL(5)=40dB; I_OpenLoop.bodex; Bode 100 [SerNo: LG278C]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

Sweep
Start Frequency :
Stop Frequency :
Center Frequency : 20.000050 MH
Span :
Sweep Mode :
Number of Points :
Configuration
Level :
Attenuator CH1 :
Attenuator CH2 :
Receiver Bandwidth :
Measurement
Reference Resistance :

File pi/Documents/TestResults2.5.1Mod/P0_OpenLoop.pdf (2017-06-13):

# Frequency Sweep

100.000 Hz 40.000 MHz; 39.999900 MH Logarithmic 201; -22.00 dBm 20 dB 20 dB 10 Hz; 50.00 Ohm; Gain; Mag(dB); Phase(°); Cursor 1 :; 23.130522 MHz; Cursor 2 : Delta :; Cursor; Calibration Probe : User :; - - Device Settings; DUT delay : Impedance CH1 : Impedance CH2 : Switch CH1 : Switch CH2 :; 0.00 s 1 MOhm 1 MOhm Internal CH2; Frequency; Trace 1; Trace 2; Measurement; Format; Imp.; Trace; Comment; P_GAIN=0dB; P0_OpenLoop.bodex; Bode 100 [SerNo: LG278C]; TR1: Mag(Gain); TR2: Phase(Gain)

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

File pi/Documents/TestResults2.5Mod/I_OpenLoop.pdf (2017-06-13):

# Frequency Sweep

Center Frequency :; Level : Attenuator CH1 : Attenuator CH2 : Receiver Bandwidth :; Reference Resistance :; 100.000 Hz 40.000 MHz; 39.999900 MH Logarithmic 201; -10.00 dBm 20 dB 20 dB 300 Hz; 50.00 Ohm; Gain; Mag(dB); Phase(°); Cursor 1 :; 1.396822 MHz; Cursor 2 : Delta :; Configuration; Measurement; Cursor; Calibration Probe : User :; Device Settings DUT delay : Impedance CH1 : Impedance CH2 : Switch CH1 : Switch CH2 :; 0.00 s 1 MOhm 1 MOhm Internal CH2; Frequency; Trace 1; Trace 2; Format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

Sweep
Start Frequency :
Stop Frequency :
Span :
Sweep Mode :
Number of Points :

IGAIN=20dB, PGAIN=-60dB, LFGL(4)
=30dB, IUGC(10)=100kHz

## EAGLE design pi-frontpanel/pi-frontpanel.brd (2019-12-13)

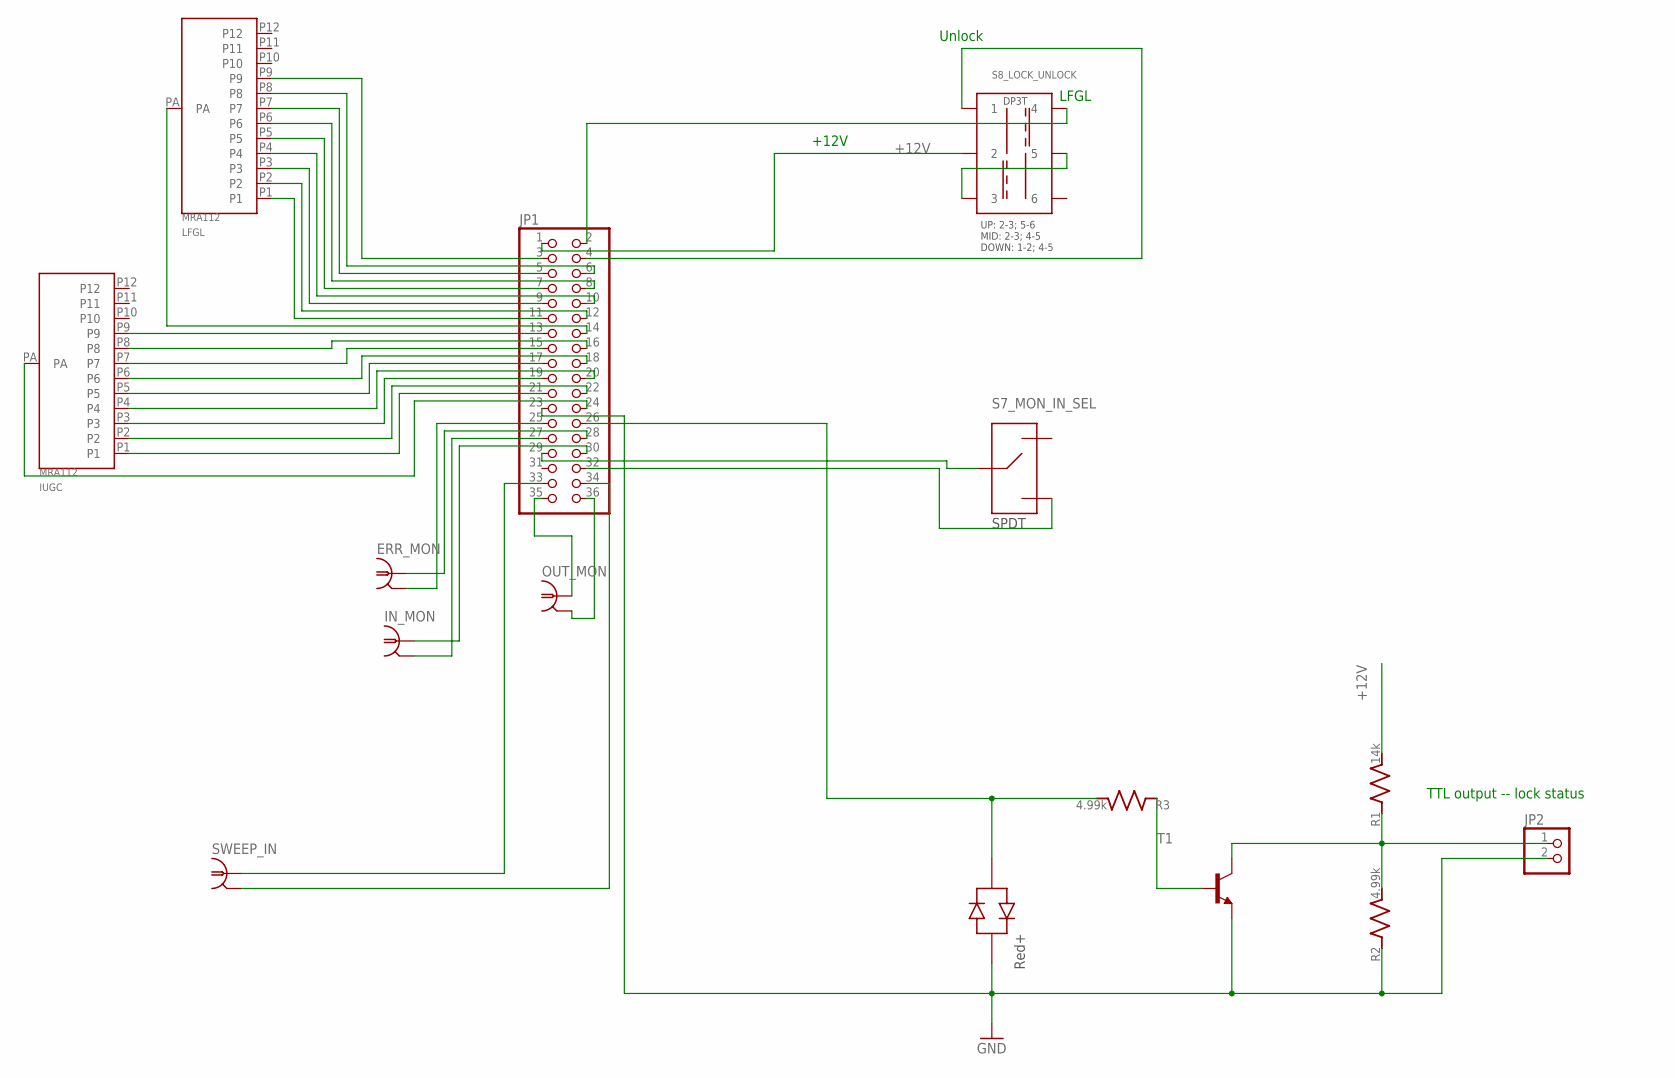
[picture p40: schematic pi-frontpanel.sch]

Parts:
ERR_MON: BNC-V; PARTNO A32262-ND
IN_MON: BNC-V; PARTNO A32262-ND
IUGC: MRA112; PARTNO 360-2368-ND
JP1: PINHD-2X18; 2X18; PARTNO S7086-ND
JP2: PINHD-1X2; 1X02; PARTNO A1921-ND
LED: SSL-LX5093IGW; LED-TH; PARTNO 67-2207-ND
LFGL: MRA112; PARTNO 360-2368-ND
OUT_MON: BNC-V; PARTNO A32262-ND
R1: 14k; R_1206; PARTNO P14.0KFCT-ND
R2, R3: 4.99k; R_1206; PARTNO P4.99KFCT-ND
S7_MON_IN_SEL: SPDT; SPDT_LUG; PARTNO 450-1523-ND
S8_LOCK_UNLOCK: DP3T; SP3T_LUG
SWEEP_IN: BNC-V; PARTNO A32262-ND
T1: MMBT2222ALT1-NPN-SOT23-BEC; SOT23-BEC; PARTNO MMBT2222A-FDICT-ND

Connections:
+12V: JP1.1, R1.P$2 (2), S8_LOCK_UNLOCK.2
GND: JP1.23, JP2.2, LED.P$2 (RED+), R2.P$1 (1), T1.E
unnamed: S8_LOCK_UNLOCK.3, S8_LOCK_UNLOCK.5
unnamed: JP1.3, LFGL.P9
unnamed: JP2.1, R1.P$1 (1), R2.P$2 (2), T1.C
unnamed: R3.P$1 (1), T1.B
unnamed: JP1.26, LED.P$1 (GREEN+), R3.P$2 (2)
unnamed: JP1.6, LFGL.P8
unnamed: JP1.5, LFGL.P7
unnamed: JP1.8, LFGL.P6
unnamed: JP1.7, LFGL.P5
unnamed: JP1.10, LFGL.P4
unnamed: JP1.11, LFGL.P1
unnamed: JP1.9, LFGL.P3
unnamed: JP1.12, LFGL.P2
unnamed: IUGC.P9, JP1.13
unnamed: JP1.14, LFGL.PA
unnamed: IUGC.P8, JP1.16
unnamed: IUGC.P7, JP1.15
unnamed: IUGC.P6, JP1.18
unnamed: IUGC.P5, JP1.17
unnamed: IUGC.P4, JP1.20
unnamed: IUGC.P3, JP1.19
unnamed: IUGC.P2, JP1.22
unnamed: IUGC.P1, JP1.21
unnamed: IUGC.PA, JP1.24
unnamed: IN_MON.2, JP1.27
unnamed: IN_MON.1, JP1.30
unnamed: ERR_MON.2, JP1.25
unnamed: ERR_MON.1, JP1.28
unnamed: JP1.36, OUT_MON.2
unnamed: JP1.35, OUT_MON.1
unnamed: JP1.34, SWEEP_IN.2
unnamed: JP1.33, SWEEP_IN.1
unnamed: JP1.29, S7_MON_IN_SEL.2
unnamed: JP1.32, S7_MON_IN_SEL.3
unnamed: JP1.2, S8_LOCK_UNLOCK.4
unnamed: JP1.4, S8_LOCK_UNLOCK.1

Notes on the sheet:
+12V
LFGL
Unlock
TTL output -- lock status

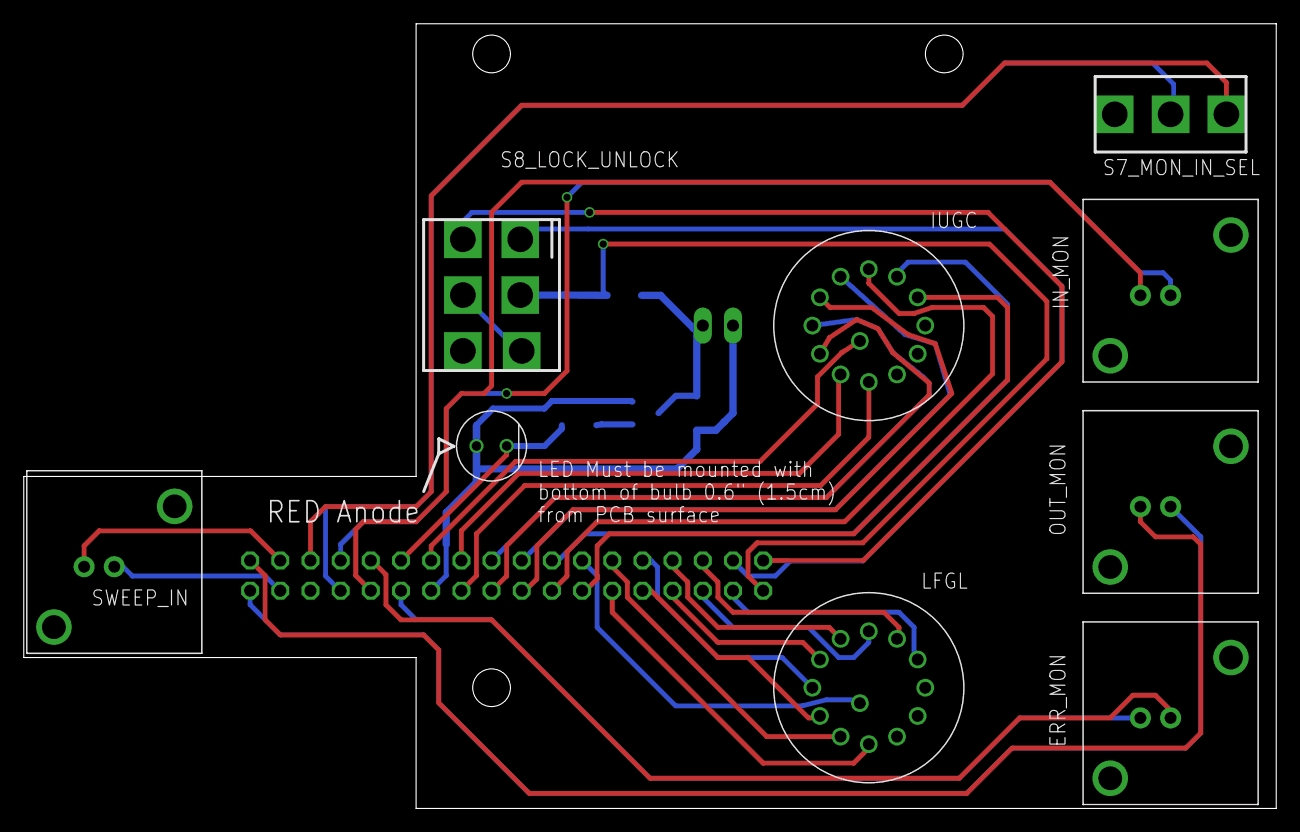
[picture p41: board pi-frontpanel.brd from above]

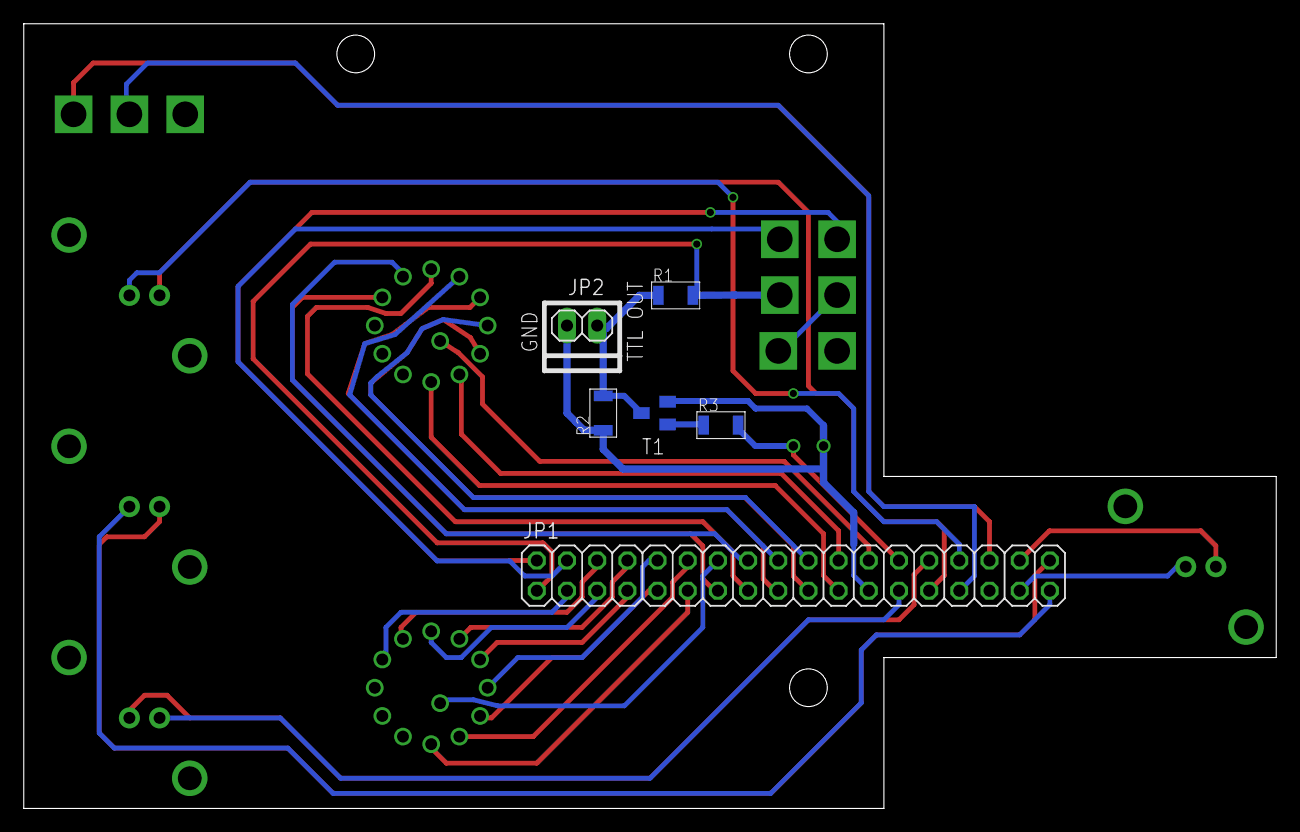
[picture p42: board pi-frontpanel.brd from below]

Board: 2 copper layers, 105.4 x 66.0 mm, 15 parts (6 on the bottom side), 38 nets.

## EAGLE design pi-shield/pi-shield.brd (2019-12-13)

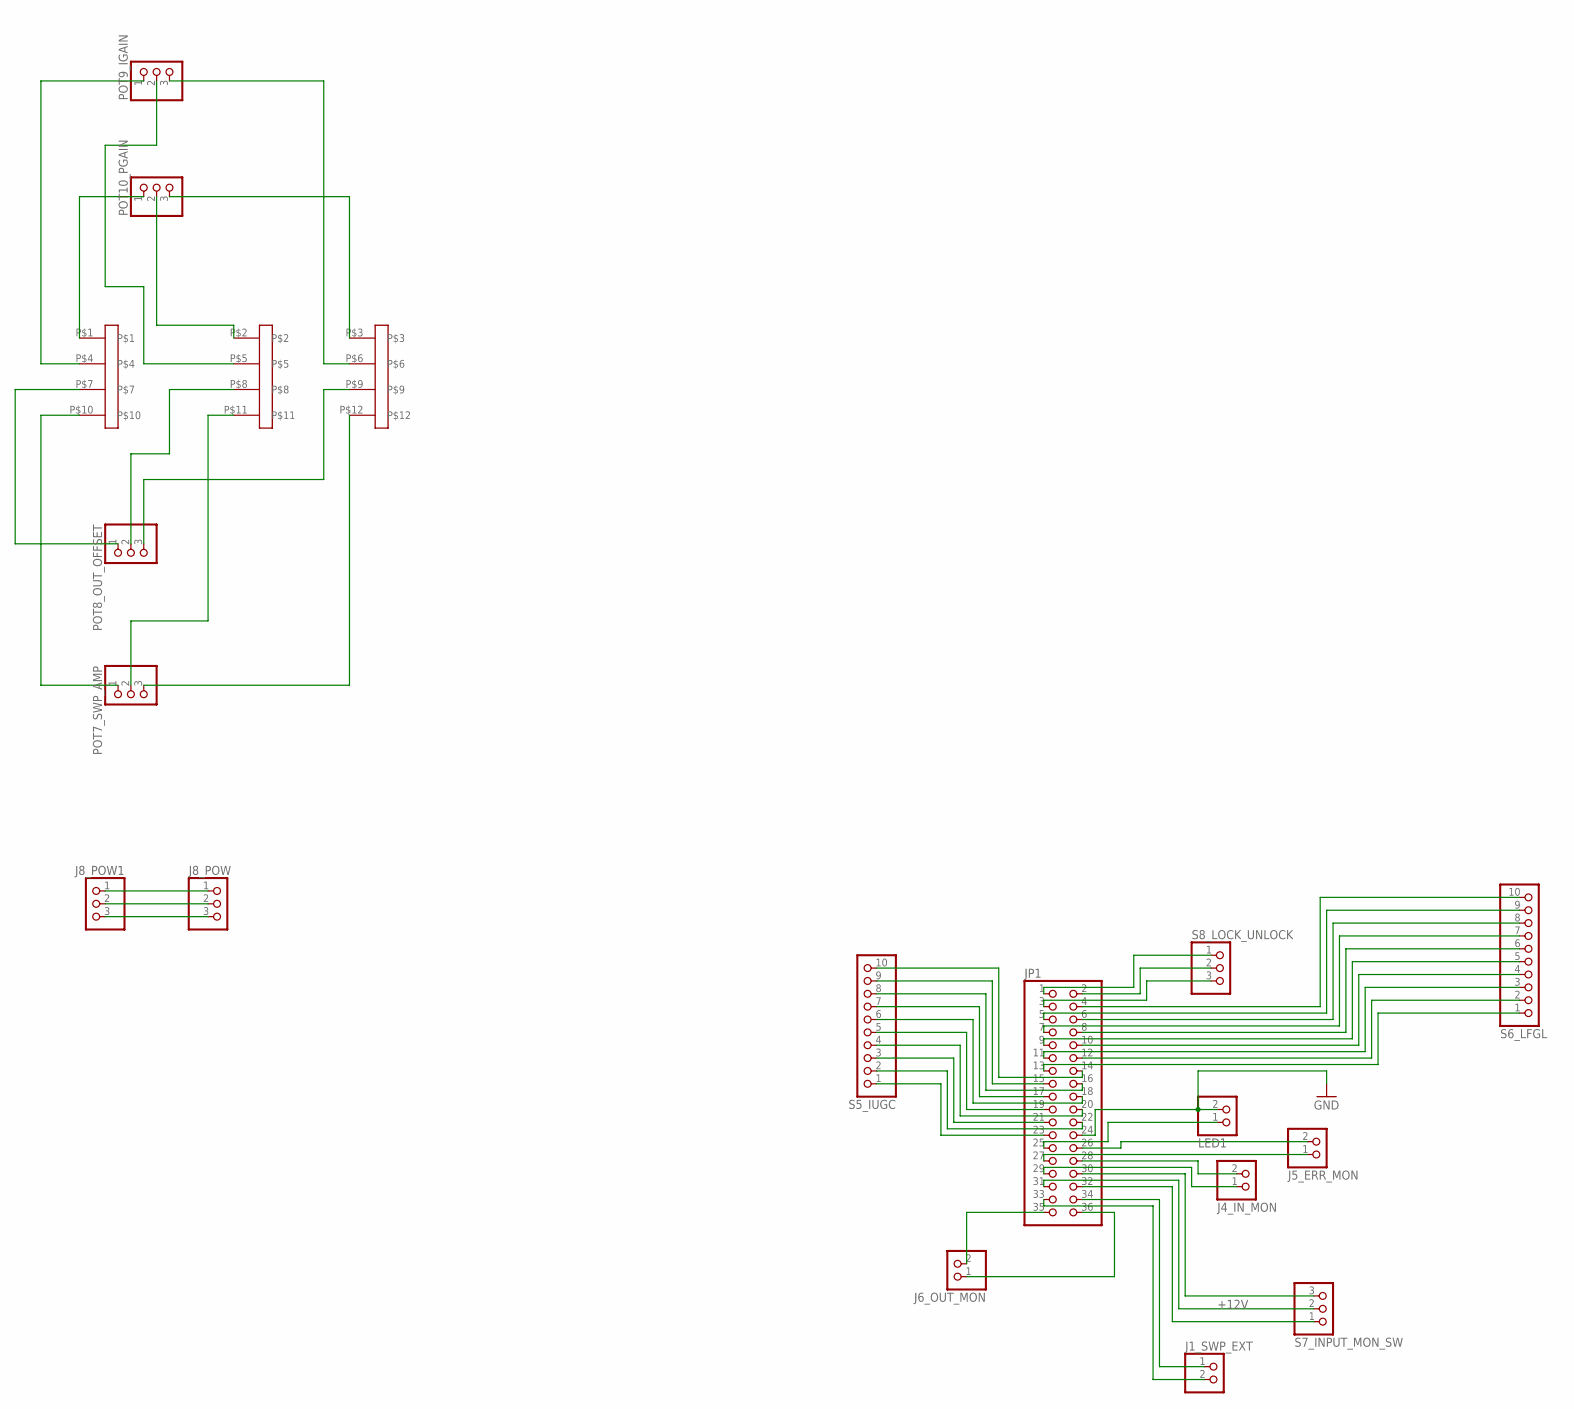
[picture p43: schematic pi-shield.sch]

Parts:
J1: PINHD-3X4; 3X04; PARTNO S7071-ND (2x)
J1_SWP_EXT, J4_IN_MON, J5_ERR_MON, J6_OUT_MON: PINHD-1X2; 1X02; PARTNO S7000-ND
J8_POW: PINHD-1X3; 1X03; PARTNO S7036-ND
J8_POW1: PINHD-1X3; 1X03; PARTNO A19470-ND
JP1: PINHD-2X18/90; 2X18/90; PARTNO S2111EC-18-ND
LED1: PINHD-1X2; 1X02; PARTNO S7000-ND
POT7_SWP_AMP, POT8_OUT_OFFSET, POT9_IGAIN, POT10_PGAIN: PINHD-1X3; 1X03; PARTNO S7036-ND
S5_IUGC, S6_LFGL: PINHD-1X10; 1X10; PARTNO S7008-ND
S7_INPUT_MON_SW, S8_LOCK_UNLOCK: PINHD-1X3; 1X03; PARTNO S7036-ND

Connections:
+12V: JP1.31, S7_INPUT_MON_SW.2
GND: JP1.24, LED1.2
unnamed: J8_POW.1, J8_POW1.1
unnamed: J8_POW.2, J8_POW1.2
unnamed: J8_POW.3, J8_POW1.3
unnamed: J1.P$1, POT10_PGAIN.1
unnamed: J1.P$2, POT10_PGAIN.2
unnamed: J1.P$3, POT10_PGAIN.3
unnamed: J1.P$4, POT9_IGAIN.1
unnamed: J1.P$5, POT9_IGAIN.2
unnamed: J1.P$6, POT9_IGAIN.3
unnamed: J1.P$7, POT8_OUT_OFFSET.1
unnamed: J1.P$8, POT8_OUT_OFFSET.2
unnamed: J1.P$9, POT8_OUT_OFFSET.3
unnamed: J1.P$10, POT7_SWP_AMP.1
unnamed: J1.P$11, POT7_SWP_AMP.2
unnamed: J1.P$12, POT7_SWP_AMP.3
unnamed: J1_SWP_EXT.1, JP1.34
unnamed: J1_SWP_EXT.2, JP1.33
unnamed: J5_ERR_MON.2, JP1.26
unnamed: J5_ERR_MON.1, JP1.27
unnamed: J4_IN_MON.2, JP1.28
unnamed: J4_IN_MON.1, JP1.29
unnamed: JP1.30, S7_INPUT_MON_SW.3
unnamed: JP1.32, S7_INPUT_MON_SW.1
unnamed: JP1.4, S6_LFGL.10
unnamed: JP1.5, S6_LFGL.9
unnamed: JP1.6, S6_LFGL.8
unnamed: JP1.7, S6_LFGL.7
unnamed: JP1.8, S6_LFGL.6
unnamed: JP1.9, S6_LFGL.5
unnamed: JP1.10, S6_LFGL.4
unnamed: JP1.11, S6_LFGL.3
unnamed: JP1.12, S6_LFGL.2
unnamed: JP1.13, S6_LFGL.1
unnamed: JP1.14, S5_IUGC.10
unnamed: JP1.15, S5_IUGC.9
unnamed: JP1.1, S8_LOCK_UNLOCK.1
unnamed: JP1.16, S5_IUGC.8
unnamed: JP1.17, S5_IUGC.7
unnamed: JP1.18, S5_IUGC.6
unnamed: JP1.19, S5_IUGC.5
unnamed: JP1.20, S5_IUGC.4
unnamed: JP1.21, S5_IUGC.3
unnamed: JP1.22, S5_IUGC.2
unnamed: JP1.23, S5_IUGC.1
unnamed: JP1.25, LED1.1
unnamed: JP1.2, S8_LOCK_UNLOCK.2
unnamed: JP1.3, S8_LOCK_UNLOCK.3
unnamed: J6_OUT_MON.2, JP1.35
unnamed: J6_OUT_MON.1, JP1.36

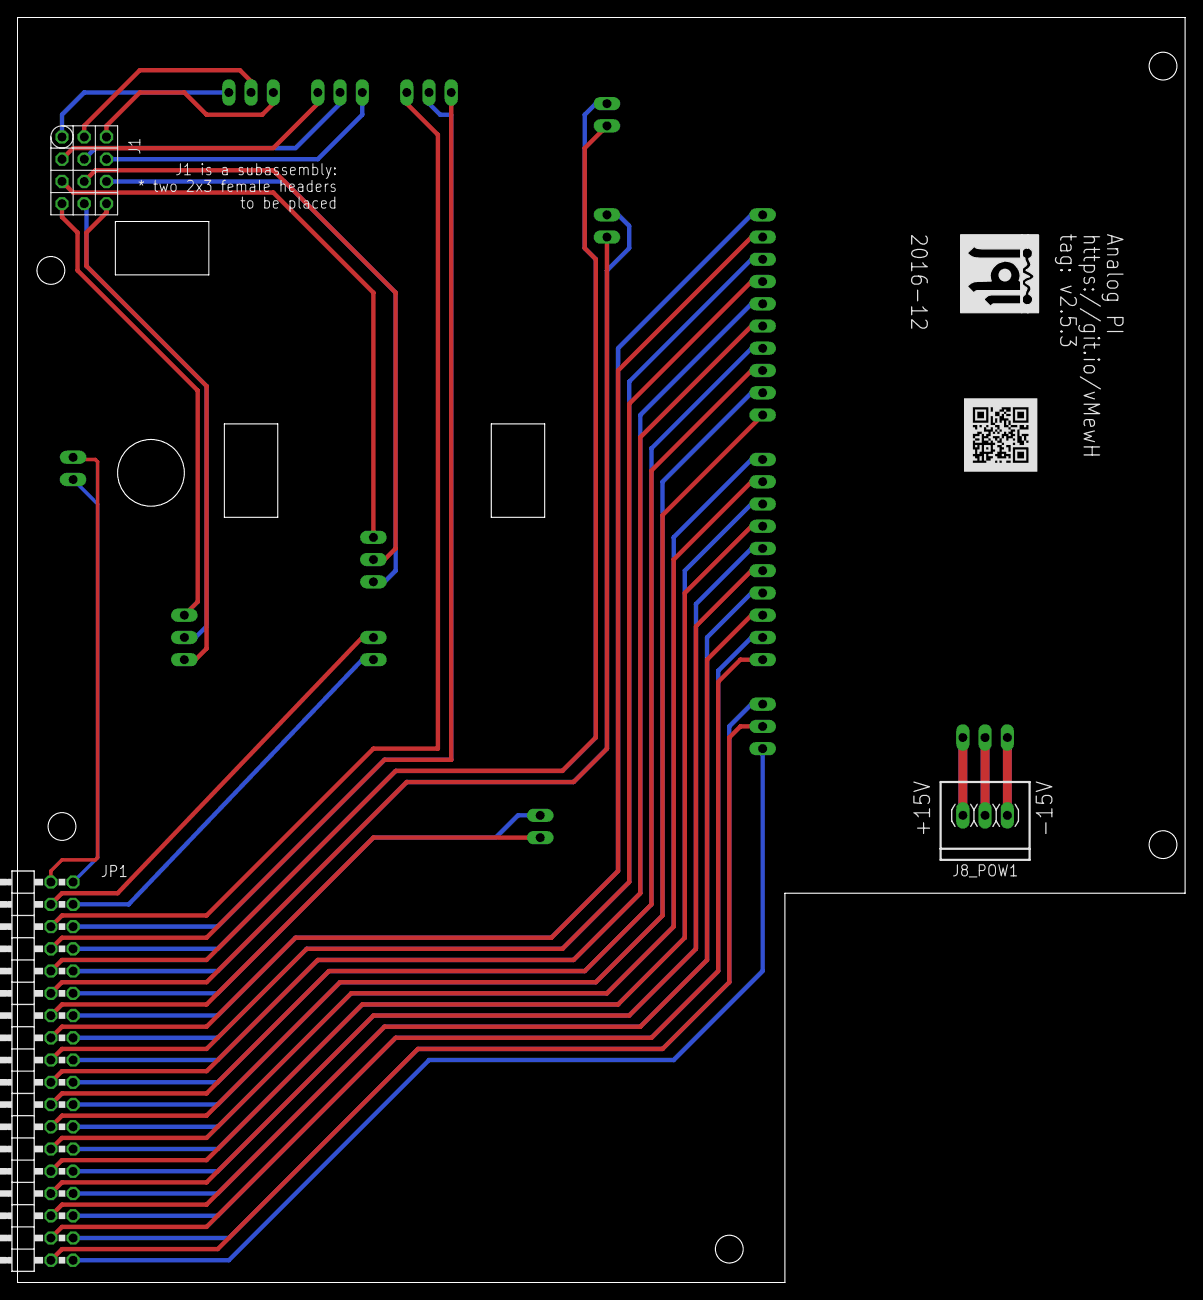
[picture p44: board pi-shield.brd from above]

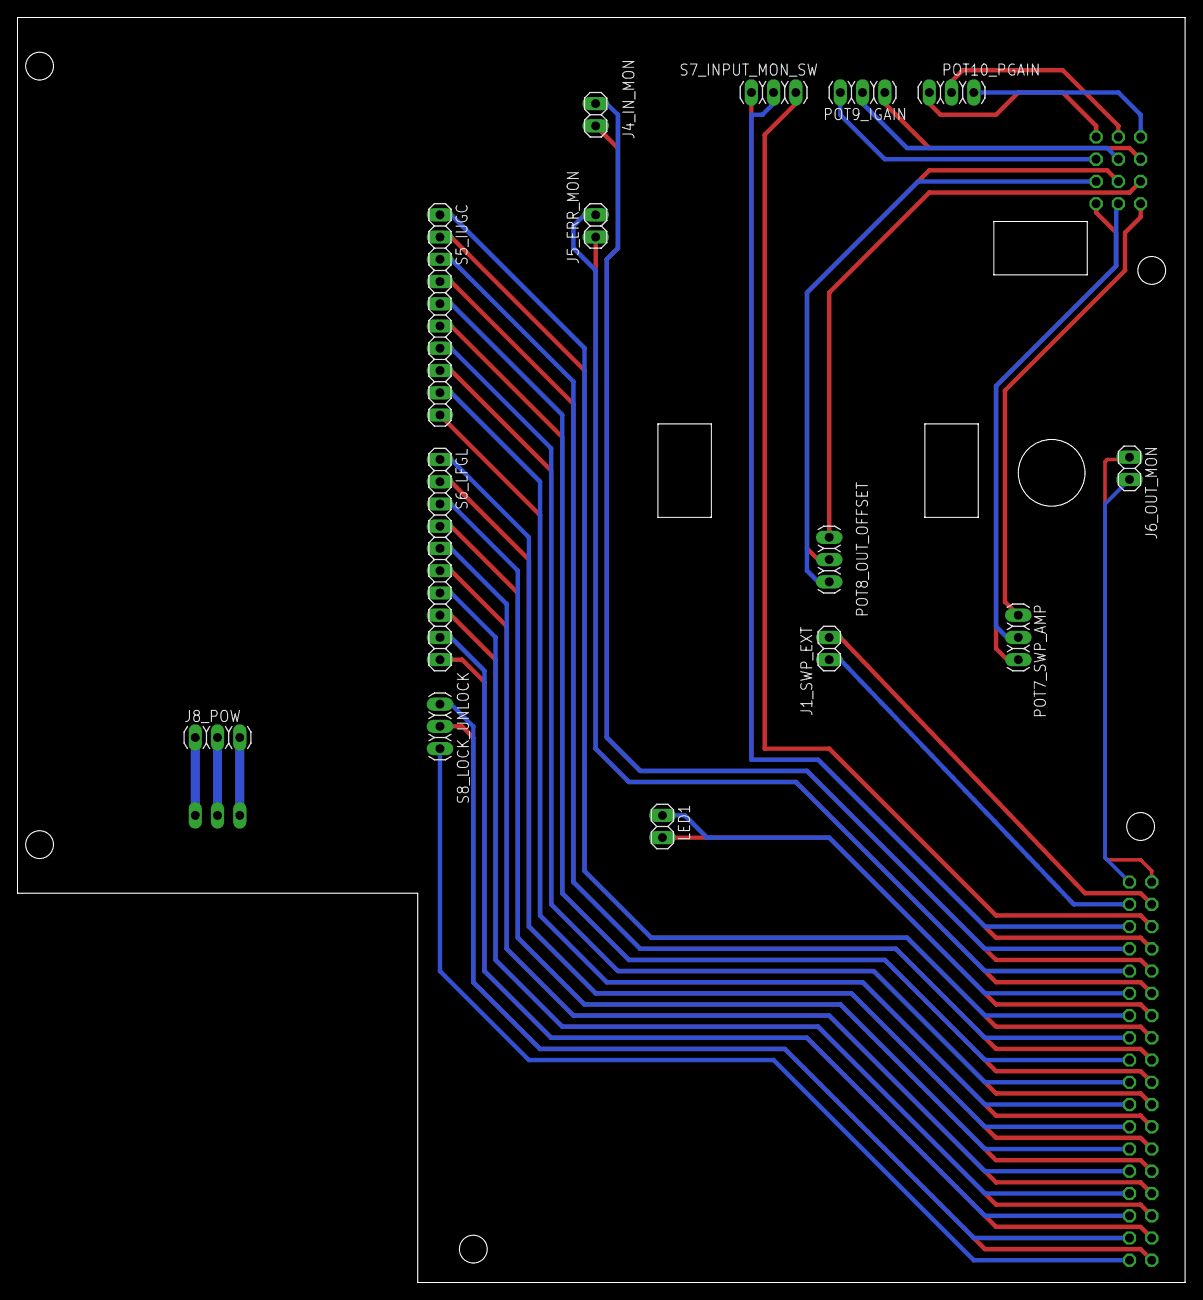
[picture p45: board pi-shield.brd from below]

Board: 2 copper layers, 133.3 x 144.4 mm, 19 parts (14 on the bottom side), 51 nets.

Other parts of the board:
U$1: QR-HTTPS://GIT.IO/VMEWH-LIGHT-SILK
U$2: JQI_LOGO_NEGATIVE-SILKSCREEN

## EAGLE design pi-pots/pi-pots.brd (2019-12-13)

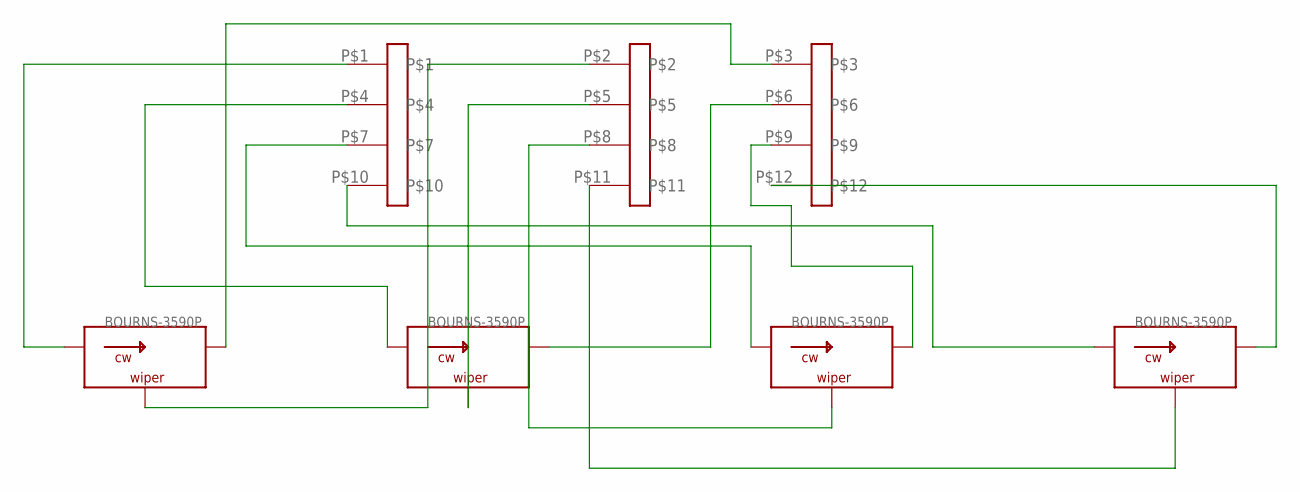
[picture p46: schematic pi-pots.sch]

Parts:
I_GAIN: BOURNS-3590P; 3590P; PARTNO 3590P-1-103L-ND
J1: PINHD-3X4; 3X04; PARTNO 952-2121-ND (2x)
OUTPUT_OFFSET: BOURNS-3590P; 3590P; PARTNO 3590P-1-103L-ND
P_GAIN: BOURNS-3590P; 3590P; PARTNO 3590P-1-103L-ND
SWEEP_AMP: BOURNS-3590P; 3590P; PARTNO 3590P-1-103L-ND

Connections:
unnamed: J1.P$1, P_GAIN.1
unnamed: I_GAIN.1, J1.P$4
unnamed: J1.P$7, OUTPUT_OFFSET.1
unnamed: J1.P$10, SWEEP_AMP.1
unnamed: J1.P$2, P_GAIN.2
unnamed: I_GAIN.2, J1.P$5
unnamed: J1.P$8, OUTPUT_OFFSET.2
unnamed: J1.P$11, SWEEP_AMP.2
unnamed: J1.P$3, P_GAIN.3
unnamed: I_GAIN.3, J1.P$6
unnamed: J1.P$9, OUTPUT_OFFSET.3
unnamed: J1.P$12, SWEEP_AMP.3

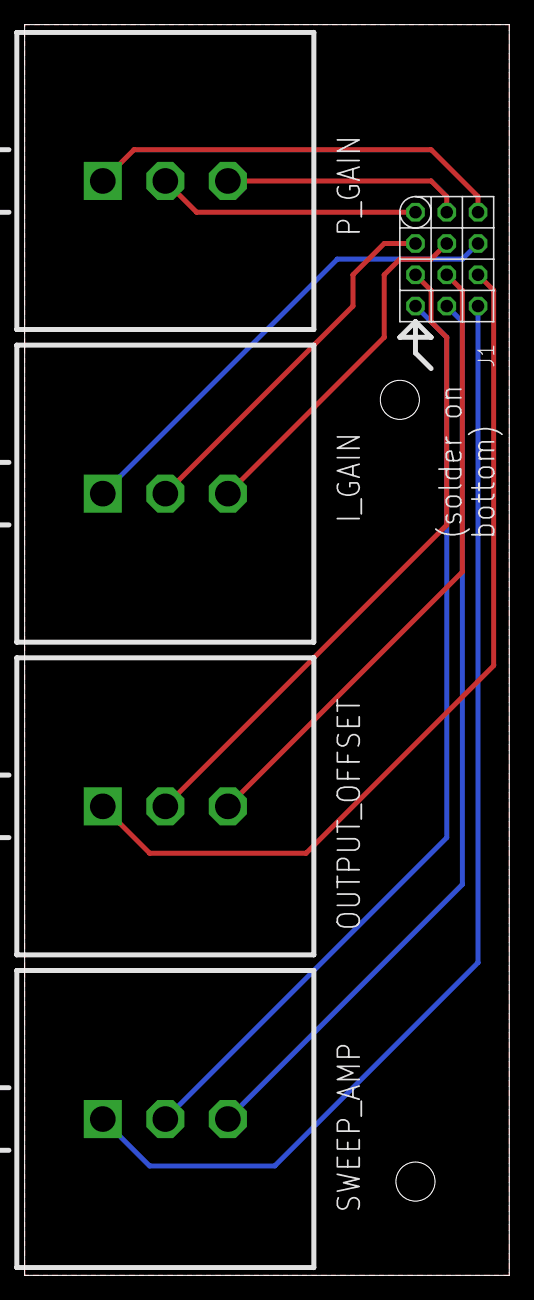
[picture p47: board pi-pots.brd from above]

Board: 2 copper layers, 39.4 x 101.6 mm, 5 parts (0 on the bottom side), 12 nets.

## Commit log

2017-06-13 Added current snapshot of project
    [PI_BOM_1MRInputImpedance.xlsx, PI_BOM_1MRInputImpedanceOPA172.xlsx, PI_BOM_50RInputImpedance.xlsx, PI_Board_Outline.gbr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]
2017-06-13 added screenshot of enclosure
2018-04-10 Removed outdated gerber files and added drill file
    [PI_Board_Outline.gbr, PI_Copper1_Top.gbr, PI_Copper2_InnerTop.gbr, PI_Copper3_InnerBottom.gbr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]
2019-12-13 Calibration Windows
    I've opened up windows above POT1-3 and U9, pin 10. The windows allow access to the pots and U9 for initial calibration of the PI controller.
    DSB
    [pi-frontpanel.brd, pi-pots.brd, pi-shield.brd]
